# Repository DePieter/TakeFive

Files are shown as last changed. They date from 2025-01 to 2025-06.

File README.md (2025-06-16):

# Take Five

Take Five is een innovatief systeem dat zorgverleners in woonzorgcentra helpt hun stressgrens beter te bewaken door stress op een niet-verstorende manier bespreekbaar en beheersbaar te maken via een combinatie van een slimme wearable, een realtime feedbackunit en een optionele verificator.

**Projectteam:** Demaegdt Pieter, Tops Bram, Schrijvers Finn  
**Datum:** 23/05/2025

## Samenvatting

> _Goede zorg start bij goede zelfzorg._

Zorgverleners ervaren vaak hoge werkstress, wat kan leiden tot burn-out. Omdat stress doorgaans te laat wordt herkend en aangepakt, is het belangrijk om vroegtijdige signalen zichtbaar te maken. Take Five biedt een persoonlijk hulpmiddel dat aangeeft wanneer stress echt te veel wordt, zodat zorgverleners tijdig kunnen ingrijpen.

Het systeem bestaat uit drie componenten:

- **Wearable:** detecteert fysiologische stresssignalen zoals hartslagvariatie (HVR) en cortisol. Bij een te hoog stressniveau trilt het apparaat zacht, met een aangenaam ritme. Indien de stress te lang aanhoudt, volgt een duidelijkere trilling.
- **Feedbackunit (FU):** toont enkel aan de desbetreffende gebruiker het realtime stressniveau op een visuele en discrete manier.
- **Verificator (optioneel):** stelt gebruiker in staat om zich te laten begeleiden bij wetenschappelijk onderbouwde oefeningen. De gebruiker scant zichzelf in, waarna een geschikte pauze wordt voorgesteld. Hierbij is een ingebouwde tijdslimiet per persoon om misbruik te voorkomen.

> _Take Five maakt stress zichtbaar, ondersteunt zelfzorg en draagt bij aan een gezonde, collegiale werkomgeving._

<p align="center">
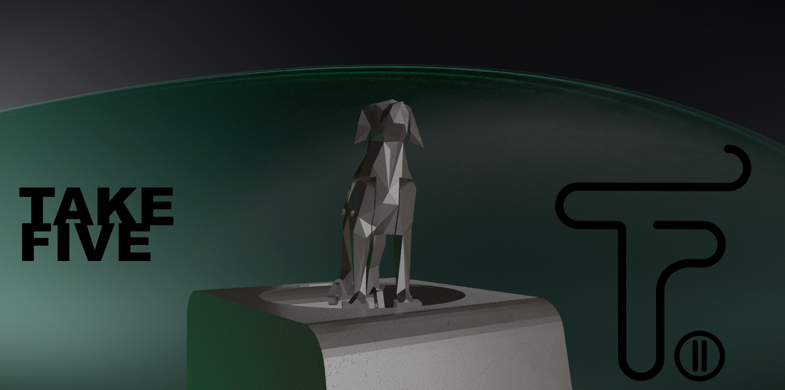
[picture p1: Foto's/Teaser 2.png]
  
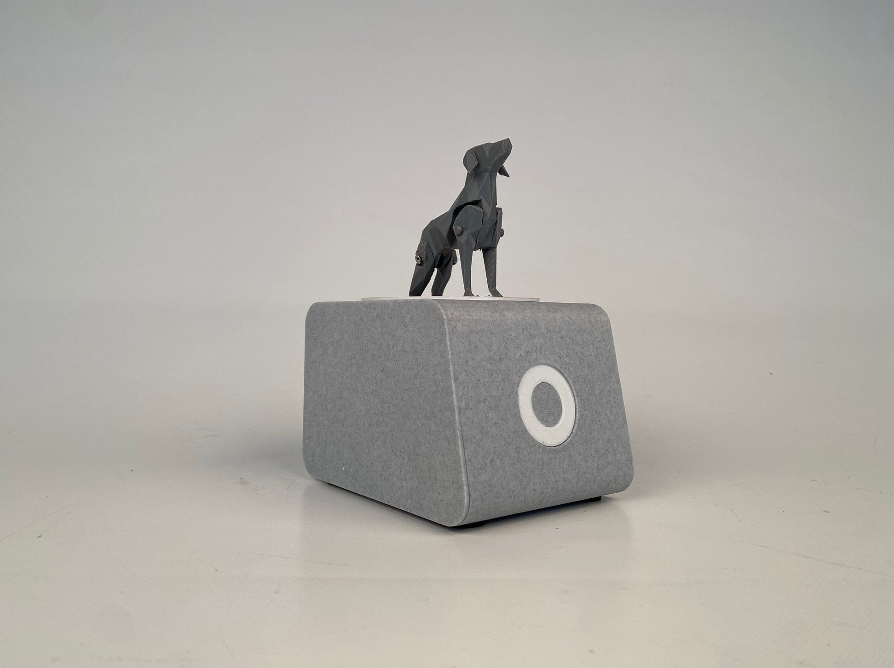
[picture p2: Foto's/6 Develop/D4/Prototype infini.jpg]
  
</p>

## Introductie

In de Belgische zorgsector loopt één op de vijf verpleegkundigen een groot risico op burn-out, en bijna 40% van de zorgverleners ervaart te veel werkstress [^1]. Dit probleem leidt tot ziekteverzuim en hoge kosten: in 2021 werd meer dan 1,8 miljard euro besteed aan arbeidsongeschiktheid door burn-out en depressie, een stijging van 59% sinds 2016 [^2]. Zorgverleners missen echter vaak directe en persoonlijke feedback over hun stressniveau, waardoor tijdig ingrijpen uitblijft.

> _Ieder jaar wordt er 280 miljoen euro gespendeerd aan burn-outs in de zorgsector._  
> _Op welke manier kan de stress bij woonzorgmedewerkers verlaagd worden zonder dat dit het werk verstoort?_

## Doelstelling

Een laagdrempelig en persoonsgericht systeem ontwikkelen dat zorgverleners helpt hun stressniveau tijdig te herkennen en te beheersen. Take Five stimuleert zelfzorg, voorkomt burn-out en versterkt het welzijn van zorgpersoneel.

Dit project focust specifiek op de toepassing binnen **woonzorgcentra (WZC)**.

[^1]: Cijfers uit de Belgische gezondheidszorgstudie 2022  
[^2]: RIZIV-rapport over arbeidsongeschiktheid, 2021

## Methodologie
In de eerste discoverfase werd de opdracht verkend aan de hand van de designchallenge 'Werkbaar Werk in de Zorg', waarbij user interviews en een literatuuronderzoek bevestigden dat stress op de werkvloer een groot probleem vormt. Methodes zoals de 5WH- en PESTEL-analyse hielpen om de onderliggende noden en kerninzichten te identificeren.
In de definitiefase werd het probleem verder verkend via een praktische aanpak met als leidraad "fall in love with the problem, not the solution." Er werden snel eerste prototypes ontwikkeld en getest in WZC Altus, waarna een verbeterde versie een week lang werd getest bij WZC De Oever. Een groepsinterview sloot de testfase af, en de verzamelde feedback vormde de basis voor het verfijnen van de design requirements die waardevol zijn in de volgende fase.
In de ontwikkelfase werd het concept verder verfijnd via gebruikerstesten en ideation-sessies met onder andere brainstorming, rollenspellen, Think Aloud en Wizard of OZ-methodes. Op basis daarvan werden prototypes uitgewerkt en getest in verschillende woonzorgcentra.
Tijdens deze tests werd gebruikgemaakt van technieken zoals Emotional Mapping met Plutchik’s Wheel, card sorting en dot-voting om emotionele reacties van gebruikers in kaart te brengen. De resultaten werden geanalyseerd met de MoSCoW-methode om prioriteiten te bepalen voor verdere verbetering.
Om ontwerpkeuzes doelgericht te evalueren, werden A/B-tests, heuristic evaluations, SUS-enquêtes en observaties ingezet. Dit leverde concrete inzichten op in wat wel en niet werkt.
Als laatst werd een online enquête verspreid om voorkeuren rond visuele en esthetische elementen te onderzoeken. Hierbij werd rekening gehouden met bias via technieken zoals desirability testing, preference testing en 5 second testing. De resultaten dienden als input voor de uiteindelijke stijl- en vormkeuzes.
De volledige ontwerpmethodologie is visueel samengevat in de onderstaande tijdlijn.

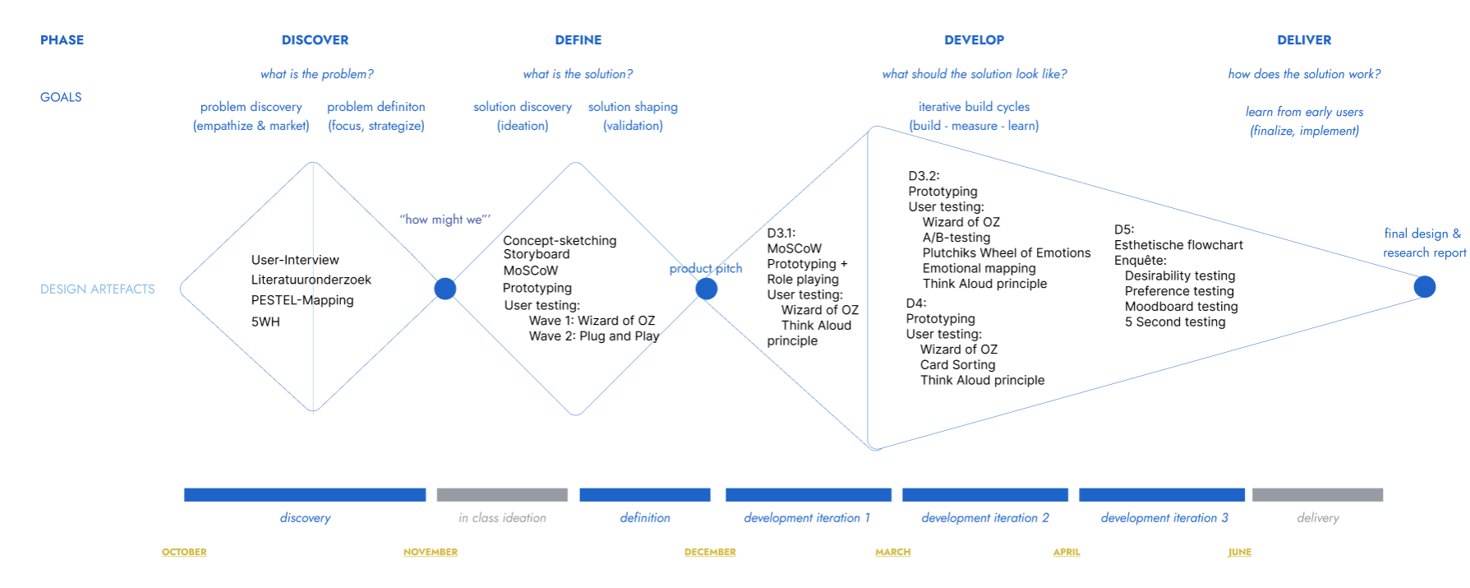
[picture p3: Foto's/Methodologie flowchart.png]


## Discovery
De discoveryfase richt zich op het definiëren van de probleemruimte, nog niet op het maken van een product. Via user interviews wordt bepaald welke problemen prioritair zijn, wat resulteert in een goed geformuleerde "how might we".

### Doelstelling
Een heldere "how might we" formuleren binnen de probleemruimte.

### Materiaal & Methoden:

-User interviews (N=3)

-Literatuuronderzoek (N=10)

### Literatuuronderzoek
Literatuuronderzoek ([Research report: literature reviews](Reports/Discovery/Research%20report%20literature%20reviews.pdf)) heeft de probleemruimte duidelijker in kaart gebracht, zo blijkt dat de zorgsector sinds 2019 kampt met een structureel hoge werkdruk, waarbij vooral het zorgpersoneel zwaar wordt getroffen. In 2023 liep 14,4% van de zorgmedewerkers risico op een burn-out[^3]. Deze problematiek is het sterkst aanwezig in woonzorgcentra, waar het aantal medewerkers met burn-outsymptomen tussen 2013 en 2023 met 7,2% is gestegen. In combinatie met de toenemende vergrijzing maakt dit de sector bijzonder kwetsbaar.

Werkdruk wordt als de belangrijkste oorzaak van werkstress geïdentificeerd. Bij 41,8% van de zorgmedewerkers heeft dit een negatieve impact op zowel hun werk-privébalans als hun algemeen welzijn[^4]. Verpleegkundigen en zorgkundigen in woonzorgcentra ervaren de hoogste werkdruk en vormen daarom de primaire doelgroep van dit project.

Sinds de coronapandemie is het langdurig ziekteverzuim met 50% gestegen. De economische impact van burn-out is aanzienlijk: jaarlijks kost het de zorgsector naar schatting 228 miljoen euro, een stijging van 10% in vijf jaar tijd. Hoewel er reeds interventies bestaan, zoals korte dagelijkse check-ups, blijkt de effectiviteit daarvan voorlopig beperkt.
In onderstaande foto wordt de probleemruimte concreet weergegeven:

<div align="center">
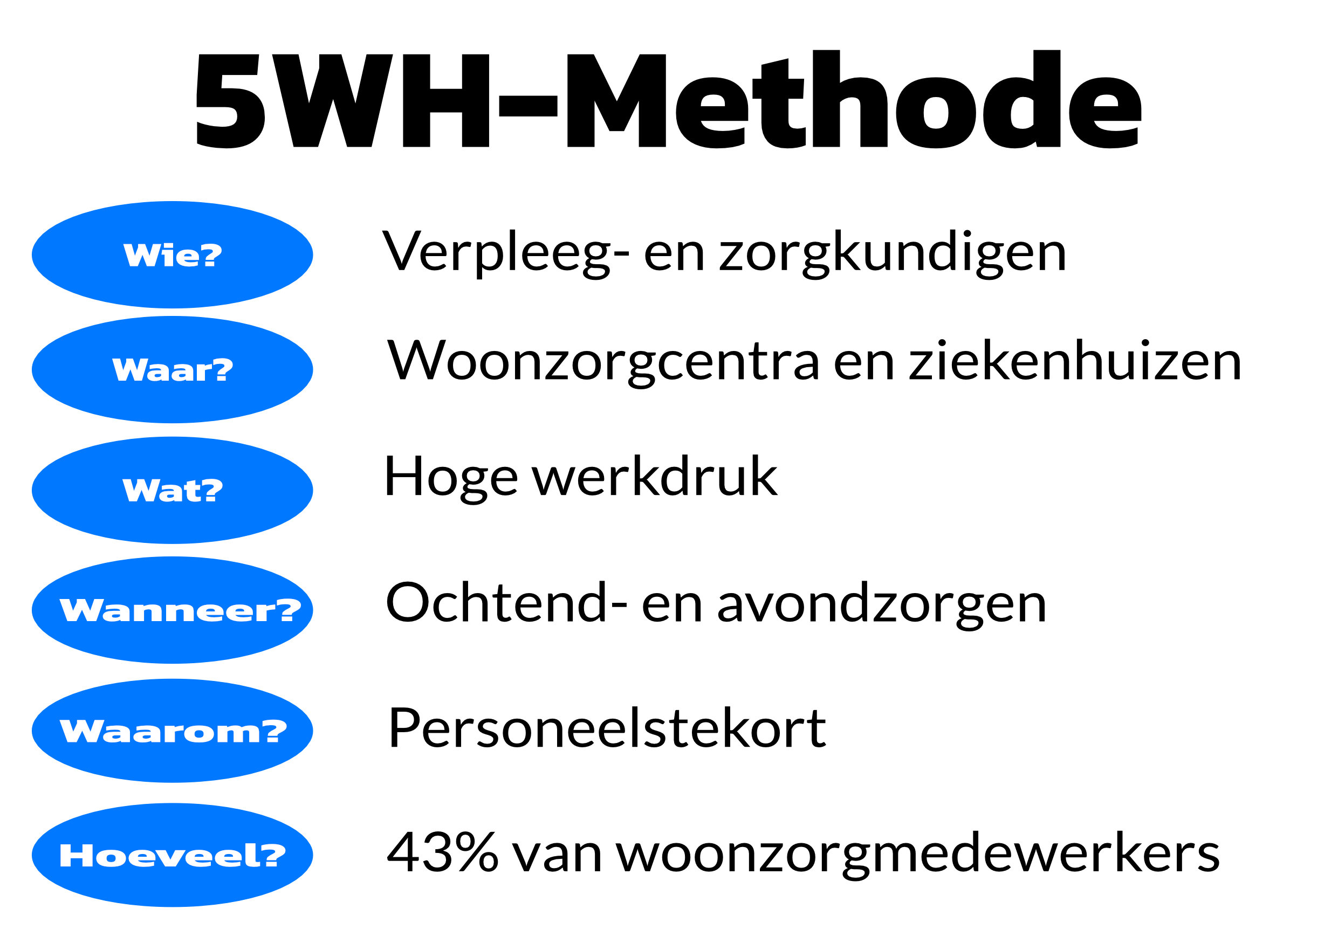
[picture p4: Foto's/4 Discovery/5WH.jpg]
  
</div>

[^3]: Vlaamse Overheid. (2023). Werkbaar werk in de zorg- en welzijnssector: Samenvatting.
[^4]: (Sociaal-Economische Raad van Vlaanderen, 2023)

### Haalbaarheid
Het is al snel duidelijk dat het in dit project van belang is om stress meetbaar te maken. Hieromtrend richt het haalbaarheidsonderzoek zich op het meten van biomarkers om werkstress en burn-out in de zorgsector objectief te detecteren. Chemische biomarkers, zoals het C-reactief proteïne in bloed of speeksel, blijken moeilijk frequent meetbaar in de praktijk. Fysische biomarkers, zoals hartslagvariabiliteit (HRV), worden daarentegen als het meest haalbaar beschouwd.

### User Interviews (N=3) 
Het doel van deze interviews was om inzicht te krijgen in hoe verpleegkundigen werkdruk ervaren en hoe dit zich vertaalt naar stress en burn-out in hun dagelijkse praktijk. Omdat stress een subjectieve ervaring is die sterk verschilt per persoon, werd gekozen voor **contextual inquiries**: een open, verkennende interviewmethode die inzichten oplevert binnen de echte werkcontext van de zorg.

Er werden drie interviews afgenomen bij **studenten verpleegkunde**, geselecteerd via **purposive sampling**. Door hun stages hebben deze studenten ervaring met verschillende afdelingen (zoals geriatrie en woonzorgcentra) en kunnen ze zowel praktijkgericht als reflectief naar het probleem kijken. Deze proef was niet bedoeld om statistisch representatief te zijn, maar om *diepgang* te bieden en **oorzaak-gevolgrelaties** te identificeren.

Bij elk interview werden **5WHY’s** en een **PESTLE-analyse** gebruikt als theoretisch kapstok:

Enkele relevante uitspraken:

>“Door personeelstekort sla ik vaak mijn korte pauze over.”

>“Als er nog veel patiënten geholpen moeten worden, stel ik mijn middagpauze uit.”

Hieruit blijkt dat vaste pauzemomenten vaak niet genomen worden wanneer werkdruk dit niet toelaat.

### PESTLE 
De **PESTLE-analyse** werd gebruikt als gesprekskader tijdens de interviews om de externe invloeden op werkdruk te analyseren. Deze dimensies werden onderzocht:

- **Political:** Beleid rond personeelsinzet en pauzeplanning
- **Economic:** Kosten van ziekteverzuim en burn-out
- **Social:** Collega's die geen pauzes nemen → sociale norm
- **Technological:** Beperkingen en kansen van wearables in de zorg
- **Legal:** Arbeidswetgeving rond rusttijden
- **Environmental:** Werkomgeving en logistieke indeling van afdelingen

Hoewel studenten niet de primaire doelgroep zijn voor het eindproduct, boden zij **waardevolle inzichten in de dagelijkse realiteit op de werkvloer**. Op basis van deze bevindingen wordt aanbevolen om in vervolgonderzoek ook leidinggevenden en directies te betrekken, om structurele oplossingen in kaart te brengen.

### Oorzaken & Gevolgen
Personeelstekort in de zorg leidt tot langere shifts en het inkorten of zelfs overslaan van pauzes, wat de ervaren stress bij zorgmedewerkers verder verergert. Hierdoor ontstaat een dubbel negatief effect: de verhoogde werkdruk zorgt niet alleen voor meer stress, maar vermindert tegelijkertijd ook de mogelijkheid tot herstel. Deze combinatie maakt de situatie bijzonder kwetsbaar. De burn-outproblematiek binnen de sector blijft toenemen en brengt stijgende kosten met zich mee, wat de noodzaak onderstreept voor preventieve maatregelen. Werkdruk die hoofdzakelijk wordt veroorzaakt door personeelstekort blijkt daarbij de voornaamste oorzaak van stress, versterkt door het ontbreken van structurele oplossingen.

### Conclusie 
Het doel van deze fase was het verkennen en afbakenen van de probleemruimte binnen de zorgsector, met een focus op werkdruk, stress en burn-out. Door middel van kwalitatieve interviews, literatuurstudie en het toepassen van de 5WHY- en PESTLE-methodologieën werd meermaals duidelijk dat:

- Pauzes een cruciale maar onderbenutte herstelstrategie zijn.
- Werkdruk toeneemt door personeelstekort en hoge zorgzwaarte.
- Technologische ondersteuning potentieel heeft, mits aangepast aan de context en noden van de gebruikers.

Deze inzichten hebben geleid tot de eerste set van **design requirements**, die de basis vormen voor het volgende projectonderdeel: de definitiefase en conceptontwikkeling van een oplossing die zorgverleners ondersteunt bij stressmanagement.
In deel [product design requirements](#product-design-requirements) staat een overzichtstabel met alle design requirements voor het eindproduct.

| ID   | Design Requirements                                                                                                                                       | Source    |
| ---- | --------------------------------------------------------------------------------------------------------------------------------------------------------- | --------- | 
| DR01 | Het ontwerp moet flexibel inspelen op wisselende personeelsbezetting gedurende de dag, zodat het inzetbaar blijft bij schommelingen in beschikbaarheid.   | Discovery |
| DR02 | Het systeem of de ruimte moet extra ondersteuning bieden tijdens piekmomenten, met name tijdens ochtend- en avondzorg, waarin de werkdruk het hoogst is.  | Discovery |
| DR03 | Het ontwerp moet flexibele pauzemomenten faciliteren, afgestemd op het actuele zorgritme, in plaats van vaste tijdsintervallen.                           | Discovery |
| DR04 | Het ontwerp moet bijdragen aan een rustgevende en stressverlagende omgeving door middel van passieve elementen zoals licht, kleur en geluid.              | Discovery |
| DR05 | Het product moet inspelen op uiteenlopende gebruikerservaringen en zowel stressverlichting (pain relief) als positieve meerwaarde (value promise) bieden. | Discovery |
| DR06 | Hartslagvariabiliteit (HRV) moet worden gebruikt als de primaire biomarker voor het meten van stressniveaus en herstelmomenten.                           | Discovery | 

## Definition
In de definitiefase worden mogelijke oplossingen onderzocht voor het eerder gedefinieerde probleem, met als doel een onderbouwde conceptkeuze. Dit concept vormt de basis voor verdere ontwikkeling in de develop- en deliverfases. De definitiefase bestaat uit drie waves, waarvan één al deels in de developfase zit. Per wave wordt het concept verder verfijnd aan de hand van theoretische modellen.

### Doelstellingen
- Ontwikkelen van prototypes die een doordacht concept representeren.
- Testen van deze prototypes in realistische scenario’s om haalbaarheid te verifiëren.
- Inzichten en gebruikersfeedback verzamelen voor verdere verbetering.

### Materiaal & methoden
Twee (+1) waves die gebruik maken van volgende methodologiën:
- Ideation
- Storyboarding
- MoSCow
- Prototyping 
- User testing (Wizard of Oz + Plug & Play)

---

### **Wave 1 (N=5)**
In deze eerste wave staat verkenning centraal: het vinden van de juiste oplossing is nog onzeker, maar de eerste ideeën, prototypes en tests vormen een cruciale stap om grip te krijgen op stress op de werkvloer.

#### Ideation
In de eerste ontwikkelingsfase werd al snel gefocust op een wearable die stress meet en feedback geeft. De vorm hangt af van de draaglocatie, die beperkt wordt door medische richtlijnen (bv. geen pols wegens infectierisico) en nauwkeurigheid van hartslagmeting. Drie locaties bleven over: borst, bovenarm en benen. De benen vielen af vanwege mogelijke associaties met enkelbanden.
Vervolgens werden snel eenvoudige schetsen gemaakt om het concept visueel te verkennen.

<p align="center">
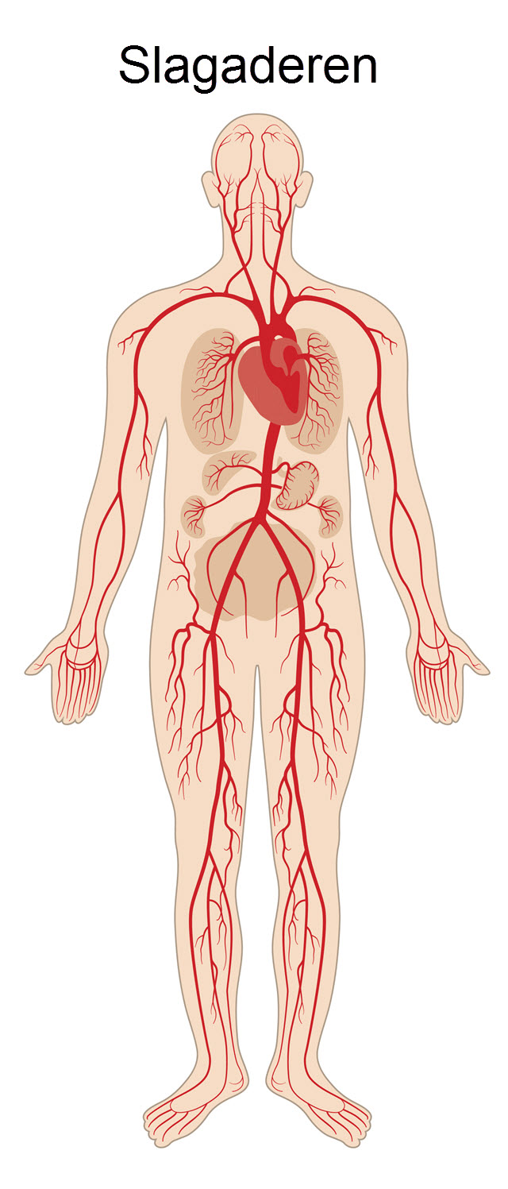
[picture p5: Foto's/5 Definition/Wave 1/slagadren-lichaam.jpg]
  
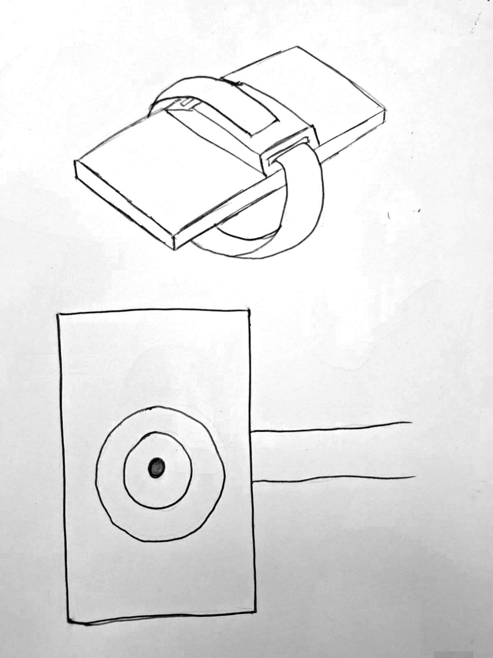
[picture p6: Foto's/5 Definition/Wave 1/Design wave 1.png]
  
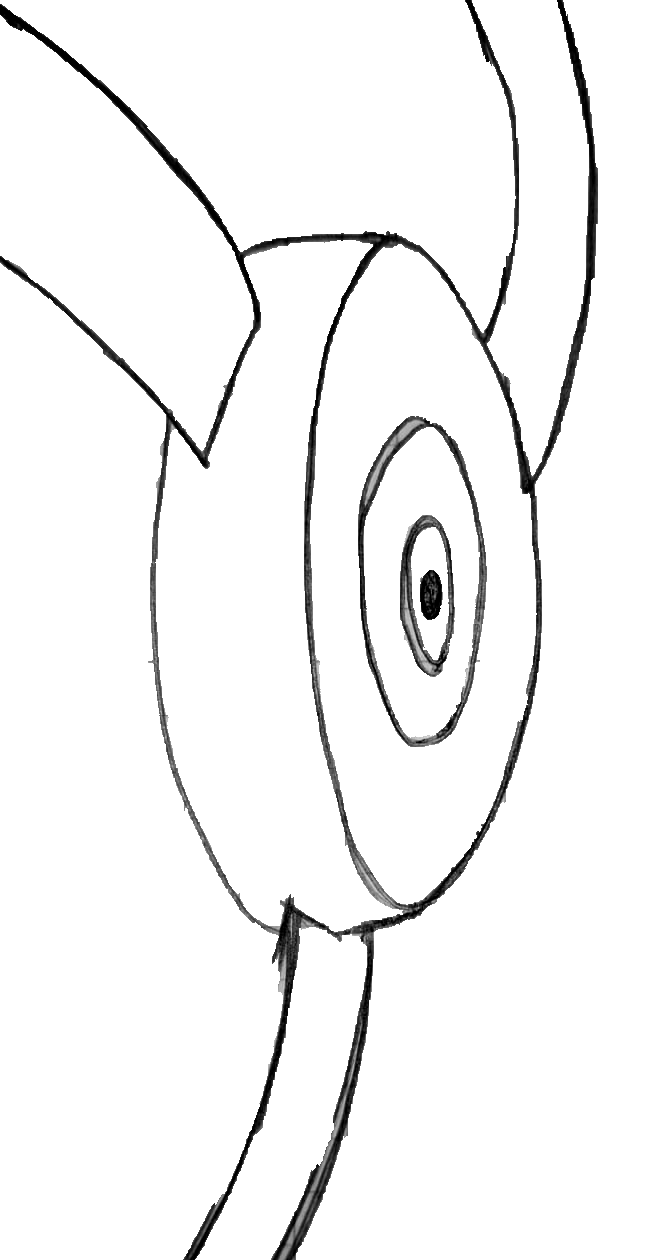
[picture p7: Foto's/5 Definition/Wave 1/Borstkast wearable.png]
  
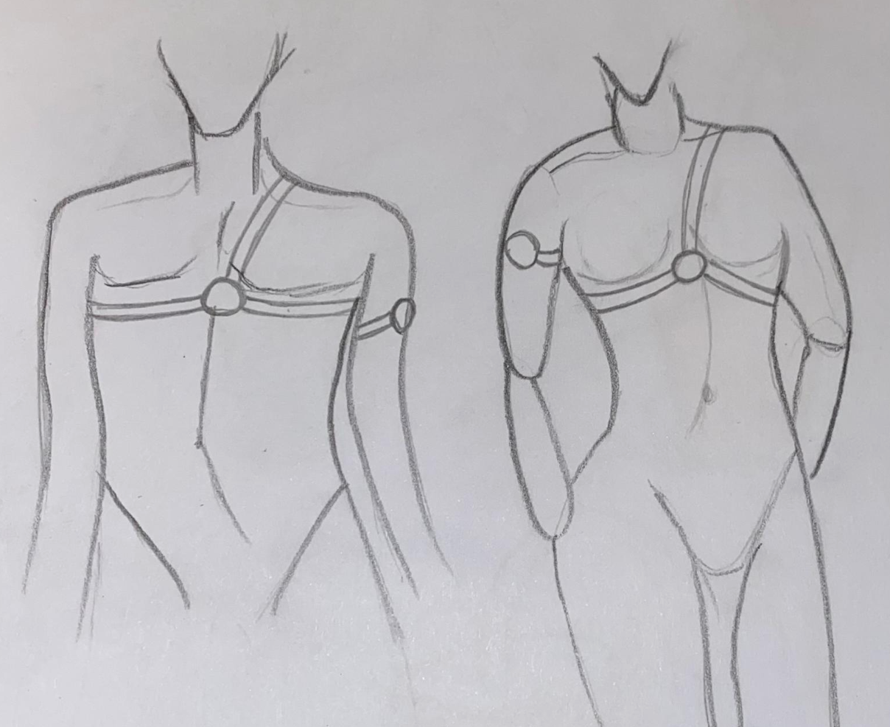
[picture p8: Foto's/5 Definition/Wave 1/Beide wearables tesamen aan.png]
  
</p>

#### Storyboarding
Om eerste onvoorziene fouten in het wearable-concept op te sporen, werd een storyboard opgesteld. Dit geeft een eerste inzicht in de werksituatie en mogelijke basisfouten.

Scenario: De zorgverlener komt aan, neemt de wearable en activeert die, waarop een lichtsignaal verschijnt. Enkele uren later volgt een trilling als teken van verhoogde stress. De zorgverlener neemt kort pauze (water drinken, diep ademhalen) en hervat daarna het werk. Na de shift wordt de wearable opgeladen.

<p align="center">
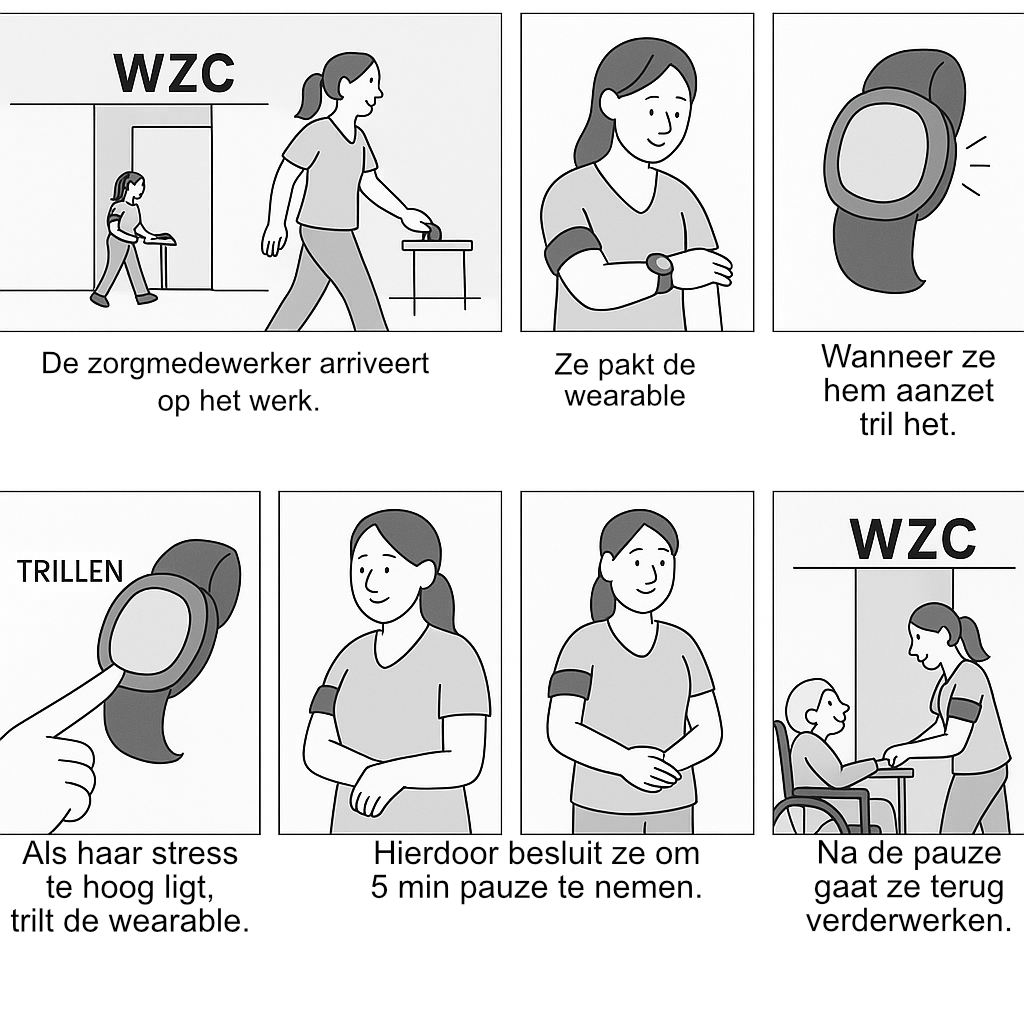
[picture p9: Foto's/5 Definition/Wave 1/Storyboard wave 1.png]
  
</p>

#### MoSCow
Om een eerste idee te krijgen van enkele voorwaarden waaraan de wearable moest voldoen, werd een eerste MoSCoW-analyse uitgewerkt.

<table>
  <tr>
    <th>Must</th>
    <td>
      - Aangename feedback<br>
      - Goedkoop<br>
      - Comfortabel zijn<br>
      - Altijd aanwezig zijn<br>
      - Oplaadbaar zijn<br>
    </td>
  </tr>
  <tr>
    <th>Should</th>
    <td>
      - Eén vaste locatie<br>
      - Makkelijk schoon te maken<br>
      - Licht geven<br>
      - Wifi-verbinding<br>
    </td>
  </tr>
  <tr>
    <th>Could</th>
    <td>
      - Leuk uitzien<br>
      - Hogerop verwittigen<br>
      - Snoozbaar zijn<br>
      - Teambuilding pauzes<br>
    </td>
  </tr>
  <tr>
    <th>Wouldn't</th>
    <td>
      - Luid zijn<br>
      - Opdringerig zijn<br>
      - Storend zijn<br>
      - Ongewenste gebruikersaantrekkingen<br>
    </td>
  </tr>
</table>

#### Prototyping
Er zijn vier verschillende prototypes ontwikkeld: twee voor de feedbackunit en twee voor de sensor. Dit maakt het mogelijk om met meerdere testpersonen tegelijk te testen.

Momenteel is het nog niet duidelijk of het voldoende is om de feedback te laten gebeuren via de wearable of dat er een externe feedbackunit nodig is. Om deze reden is er ook een extra concept voorzien bij het mken van prototypes; de feedbackunit (FU).

Voor de feedbackunit zijn alle mogelijke signaleringsmethoden geïntegreerd in twee compacte wizard of oz prototypes, die op afstand kunnen worden aangestuurd via een smartphone. Hieronder worden de prototypes weergegeven en beschreven.

<table>
  <tr>
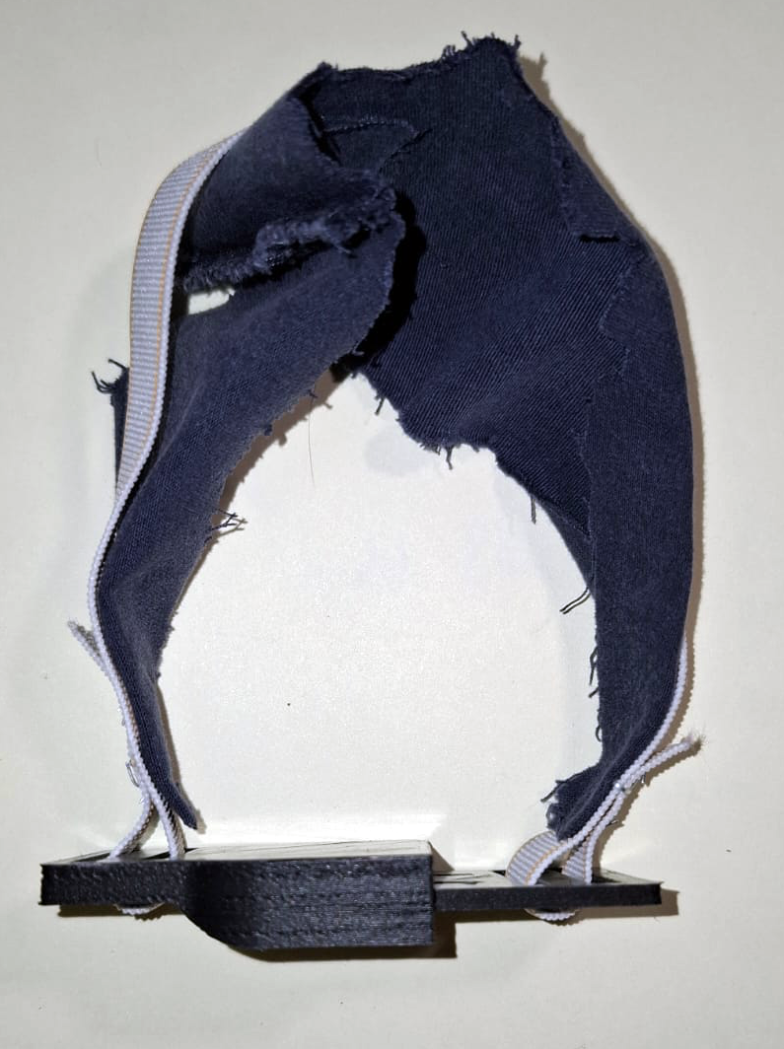
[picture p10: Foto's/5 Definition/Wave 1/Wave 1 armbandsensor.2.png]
    <td>
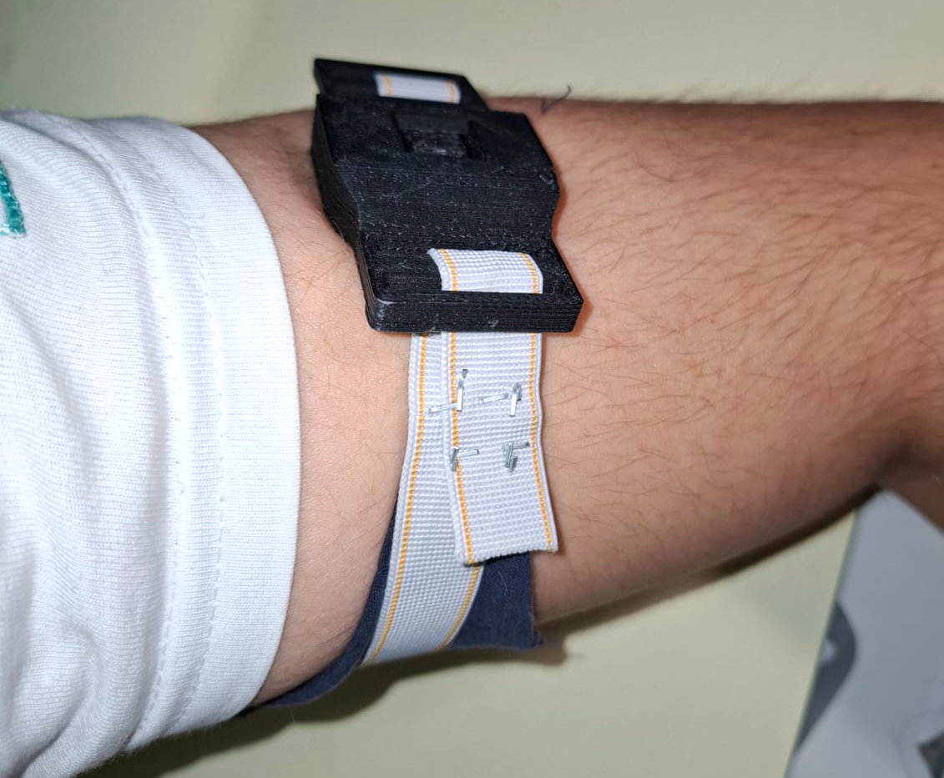
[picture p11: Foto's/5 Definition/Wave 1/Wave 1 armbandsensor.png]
	  <td>
    <td>De <b><u>armband sensor:</u></b> bestaat uit een ge-3D-printe body met een elastieken band, deze kan gedragen worden op de bovenarm.</td>
  </tr>
  <tr>
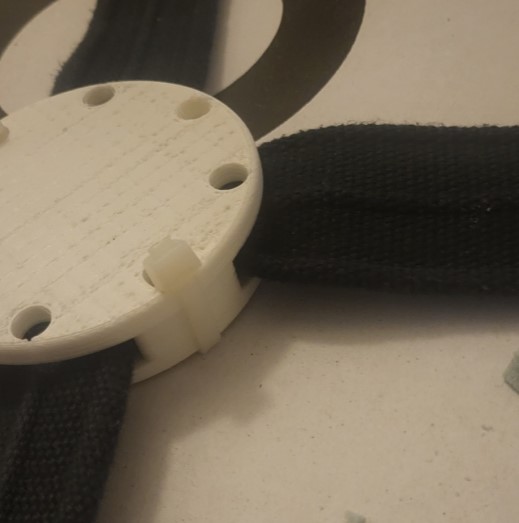
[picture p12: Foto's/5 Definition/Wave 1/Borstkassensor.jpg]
    <td>
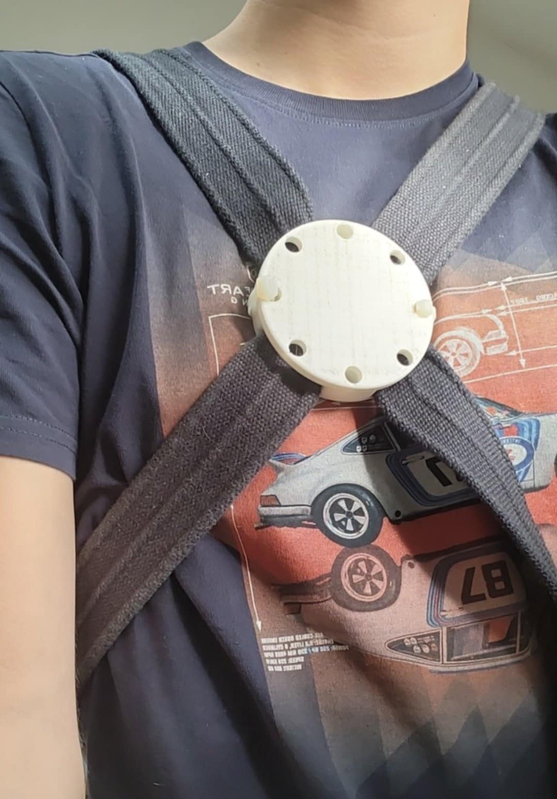
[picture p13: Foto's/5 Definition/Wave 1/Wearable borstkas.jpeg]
	  <td>
    <td>De <b><u> borstkas sensor</u></b> bestaat uit twee verstelbare riemen met een 3D-geprinte behuizing, zodat hij naar wens kan worden aangespannen. <b><u>          </td></td>
  </tr>
  <tr>
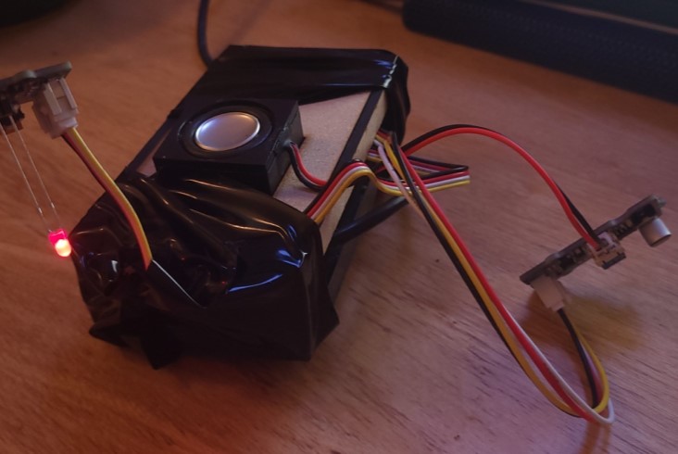
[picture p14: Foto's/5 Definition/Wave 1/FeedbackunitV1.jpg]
    <td>
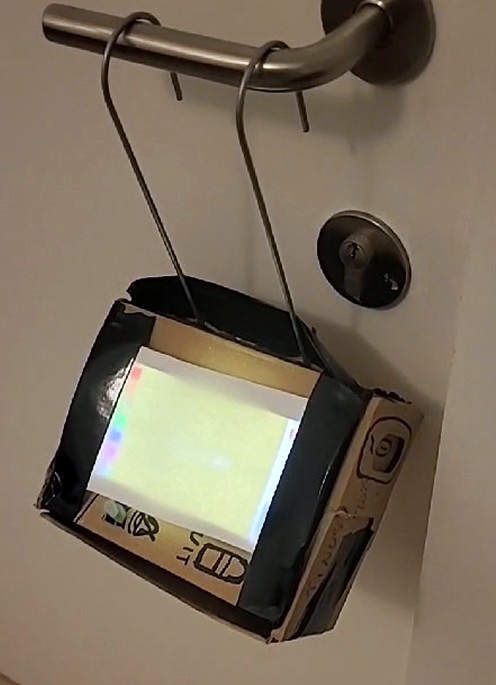
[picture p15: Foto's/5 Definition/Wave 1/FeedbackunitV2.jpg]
	  <td>
    <td>De <b><u>feedback unit's:</u></b>  bestaan uit een MDF- en een kartonnen behuizing, waarmee alle signaalmethoden, zoals geluid en licht, getest kunnen worden met Arduino en een ingebouwde gsm.    </td></td>
  </tr>
</table>

#### User testing (n=5)
Tijdens deze gebruikerstest in WZC Althus werden de eerste functionele prototypes van het stressdetectiesysteem geëvalueerd. Doel was het concept te toetsen op levensvatbaarheid, gebruiksvriendelijkheid en impact, om zo richting te geven aan verdere ontwikkeling.
Vijf zorgmedewerkers (begeleiders, opvoeders, teamleider) werden geïnterviewd na een korte introductie en informed consent. Ze vertelden over hun werk, stresservaringen, copingstrategieën en gaven feedback op de prototypes (zie [Protocol wave 1](https://github.com/DePieter/TakeFive/blob/main/Protocols/Define/Wave%201%20Protocol%20Althus.pdf)).

Tijdens het interview konden de respondenten ook de prototypes zelf ervaren. Hierbij werd gepeild naar hun ervaring met deze meldingsvormen: waren ze storend of net ondersteunend? Waren ze duidelijk en bruikbaar in een drukke werkomgeving?

Respondenten ervaren stress door tijdsdruk, onverwachte situaties en multitasking. Men herkende structurele overbelasting en gaf aan dat hun huidige strategieën vaak tekortschieten.
Het trilsignaal van de armband werd als subtiel en niet-storend ervaren, geluidssignalen als te opdringerig. Een externe feedbackunit op de zorgkar werd gezien als nuttige aanvulling, aangezien trillingen soms onopgemerkt blijven.
Meteen pauze nemen op basis van meldingen bleek zelden haalbaar, maar vroegtijdige signalering werd als waardevol beschouwd. De behoefte aan een compact, discreet en intuïtief systeem dat naadloos past in de workflow werd breed gedeeld.
De inzichten zijn verwerkt tot ontwerpvereisten in 
[Rapport wave 1](https://github.com/DePieter/TakeFive/blob/main/Reports/Define/Rapport%20Althus.pdf).

> _"Het zou handig zijn als een systeem stress kan detecteren voordat het te erg wordt."._

> _"Een discreet signaal, zoals een trilling, zou helpen zonder cliënten te storen."._

> _"Als ik zou kunnen kiezen, kies ik voor de armband."._

> _"Een discreet signaal, zoals een trilling, zou voorkomen dat gebruikers geïrriteerd of boos worden."._

> _"Ik vind de externe feedbackunit een goed concept omdat ik in the heat of the moment zo'n trilling via enkel de wearable niet altijd zal opmerken vrees ik"._

#### Conclusies & implicaties:
Het hoofddoel van wave 1 was om de conceptuele werking goed of af te keuren. Daarbij werd onderzocht of het gebruik van een feedbackunit effectief en zinvol is. Dankzij waardevolle inzichten uit onder andere de eerste gebruikerstesten, levert deze test niet alleen een antwoord op de hoofdvraag, maar maakt ze het ook mogelijk om al enkele ontwerpdetails vast te leggen. De conclusie is dat het concept verder uitgewerkt kan worden, met de feedbackunit als essentieel element om triggerblindheid te voorkomen. Daarbij moet rekening gehouden worden met de [Product design requirements](#product-design-requirements) waarvan hieronder de belangrijkste staan weergegeven:

| ID    | Design Requirements                                                                 | Source   | Date       |
|-------|---------------------------------------------------------------------------------------|----------|------------|
| DR07  | Subtiel design met trilling of licht, geen geluid.                                   |          |            |
| DR12  | Klein, licht en comfortabel draagbaar ontwerp.                                       |          |            |
| DR17  | Discreet en universeel ontwerp tegen stigma.                                         |  Wave 1  | 11/12/2024 |

### **Wave 2 (N=5)**
De bekomen design requirements uit wave 1 worden hier in wave 2 gebruikt om het ontwerp te verbeteren. Hierbij werd bij benadering eenzelfde structuur zoals wave 1 toegepast.

#### Ideation
Tijdens de ideatiefase van wave 2 werd in een brainstormsessie besloten om nieuwe versies van de FU en de wearable te ontwerpen met enkele werkende, primitieve functies. Dit heeft als doel om de prototypes geschikt te maken voor een meer uitgebreide tests in een realistische werkomgeving. Nadat de twee beste concepten waren geschetst, werd onderzocht hoe deze gerealiseerd konden worden.
De FU bevatte zowel de signaalfunctie als een oplaadstation.
De wearable werd voorzien van EVA-foam, gevormd met behulp van een mal zodat het goed aansluit op het lichaam.

<p align="center">
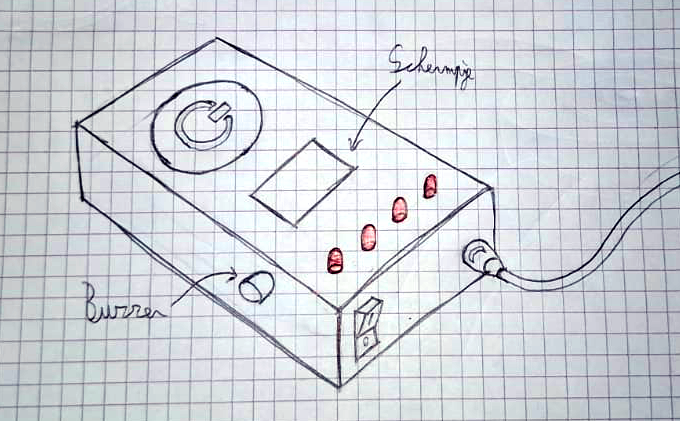
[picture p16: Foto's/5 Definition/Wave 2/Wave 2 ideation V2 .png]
  
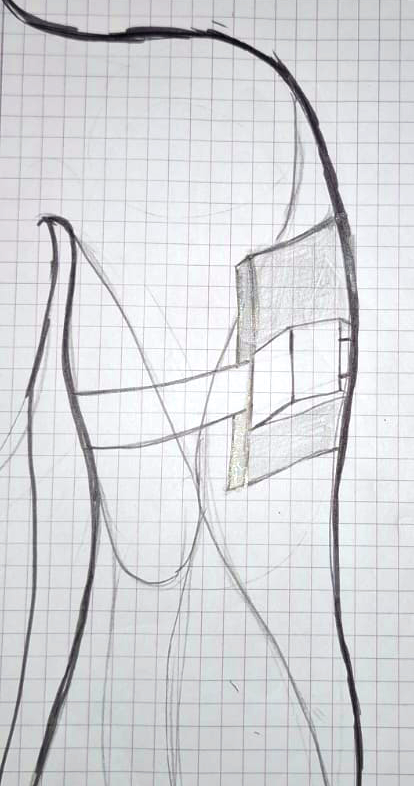
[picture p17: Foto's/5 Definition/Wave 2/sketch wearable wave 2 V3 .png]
  
</p>  

#### Prototyping
Verderwerkend op de keuzes die gemaakt zijn in de ideation, worden enkele prototypes uitgewerkt. 

<table>
  <tr>
    <td>
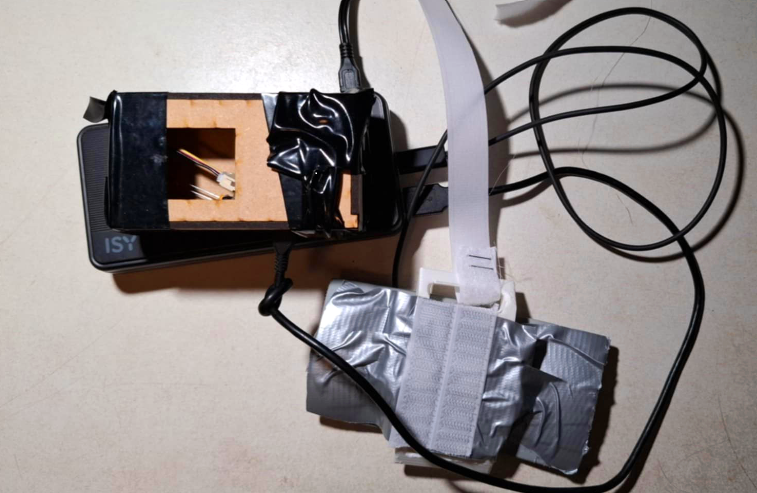
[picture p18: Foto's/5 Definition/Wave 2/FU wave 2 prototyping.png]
FU wave 2 prototyping
      
    </td>
    <td>
      De FU maakt gebruik van lichtsignalen en geluid om te communiceren. Ook beschikt de FU over een oplaadstation voor de wearable.
    </td>
  </tr>
  <tr>
    <td>
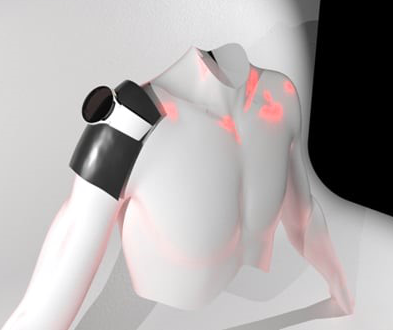
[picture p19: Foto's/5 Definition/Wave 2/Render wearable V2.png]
Render wearable V2
      
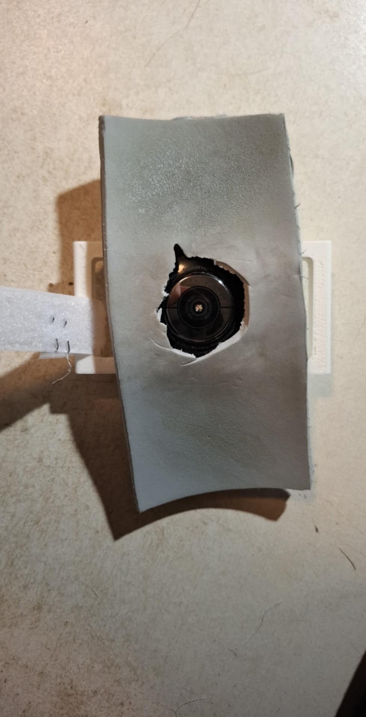
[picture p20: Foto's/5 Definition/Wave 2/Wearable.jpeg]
Wearable
      
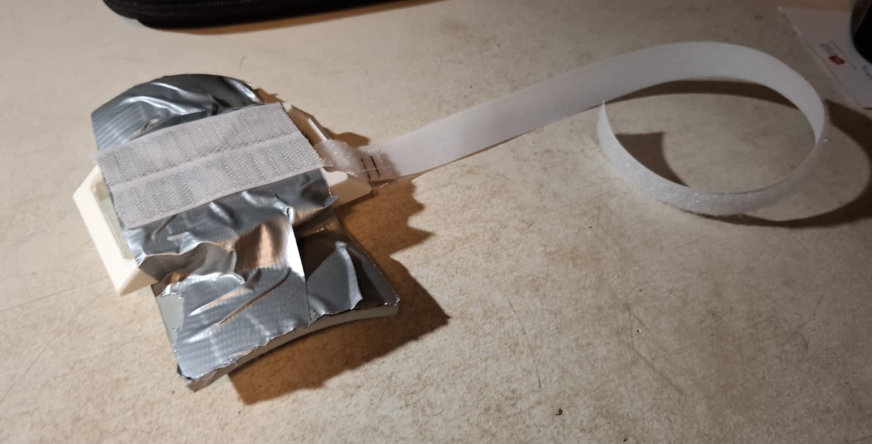
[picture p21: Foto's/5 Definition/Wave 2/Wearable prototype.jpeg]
Wearable prototype
      
    </td>
    <td>
      De wearable is vervaardigd van EVA-foam, gevormd naar de mal van een bovenarm. Daarnaast is er een smartwatchsensor geïntegreerd voor nauwkeurige stressmetingen.
    </td>
  </tr>
</table>

#### User testing (n=5)
Voor deze testfase werd een ‘Plug and Play’-protocol (zie [Protocol wave 2](https://github.com/DePieter/TakeFive/blob/main/Protocols/Define/Wave%202%20Protocol%20De%20Oever.pdf) ) ontwikkeld waarmee de zorgverleners van WZC De Oever zelfstandig aan de slag konden. Elke deelnemer kreeg een uitgebreide handleiding met instructies over het installeren van de wearable en feedbackunit, het uitvoeren van pauzeoefeningen (zoals ademhaling, korte babbel of buiten wandelen) en het invullen van een zelfevaluatie na elke oefening. De test liep over vijf dagen, waarbij deelnemers meerdere keren per dag door de feedbackunit visueel (via knipperlicht) werden aangespoord om een korte pauze te nemen.

Elke interventie werd geëvalueerd op effectiviteit via een scoreformulier. Deze kwantitatieve evaluatie werd aangevuld met kwalitatieve feedback in een afsluitend groepsgesprek.

### Conclusies & implicaties:
Deze testfase onderzocht de toepasbaarheid en integratie van het prototype in een realistische zorgcontext. Het systeem beantwoordt aan een concrete behoefte: de oefeningen hielpen gebruikers om stil te staan bij hun stressniveau en gaven rustmomenten, al verschilde de effectiviteit per persoon.
Lichtsignalen werden niet altijd opgemerkt in de drukte. Respondenten stelden subtiele extra signalen (zoals trilling of geluid) voor. Ook bleek er twijfel over de betrouwbaarheid van zelfgenomen pauzes, wat wijst op de nood aan terugkoppeling of controle in het systeem.
Belangrijke inzichten:
- De wearable was comfortabel voor korte duur, maar moet kleiner, zachter en robuuster voor langdurig gebruik.
- De impact op bewoners was nihil, wat de discretie bevestigt.
- De testopstelling was eenvoudig en werd zelfstandig beheerd.
- Gebruikers zouden het systeem aanbevelen aan collega’s.

Deze resultaten bieden input voor het verfijnen van de gebruikservaring, het verhogen van de effectiviteit en het aanscherpen van de functionele ontwerpcriteria. Het volledig verslag is terug te vinden in [Rapport wave 2](https://github.com/DePieter/TakeFive/blob/main/Reports/Define/Report%20De%20Oever.pdf)
Daarbij moet rekening gehouden worden met de [Product design requirements](#product-design-requirements) waarvan hieronder de belangrijkste staan weergegeven:

| ID    | Design Requirements                                                                                   | Source   | Date       |
|-------|-------------------------------------------------------------------------------------------------------|----------|------------|
| DR18  | Intuïtieve bediening met duidelijke pauzemeldingen in drukke omgevingen.                              |    |            |
| DR21  | Verstoort geen lopende taken en past in bestaande workflows.                                          |    |            |
| DR23  | Modulair systeem -> verwisselbaar voor dag en nacht shift                                             | Wave 2 | 23/12/2024   |

# Develop
De develop fase draait rond het verfijnen van het product. Hiervoor worden de fysieke ergonomie, de cognitieve en de sensoriële ergonomie geoptimaliseerd aan de hand van theorie, prototyping en testing. 
Deze fase bestaat uit drie opeenvolgende fases, elk met een specifieke focus:
1.	Extra Concepttest – In deze eerste fase wordt het initiële idee ter aanvulling van voorgaande definitionfase geëvalueerd en gevalideerd.
2.	Metafooronderzoek – Vervolgens wordt onderzocht welke metafoor het meest geschikt is voor de feedbackunit.
3.	Vorm- en emotieverfijning – Tot slot wordt de gekozen metafoor verfijnd op emotioneel vlak en wordt de esthetiek van het volledige prototype geoptimaliseerd.

### Doelstellingen
- Prototype verfijnen
- Belangrijkste design challenges identificeren door zowel theoretisch als praktisch onderzoek

### Materiaal & methoden
Tijdens deze fases worden verschillende methodologieën toegepast, waaronder:
- Brainstorming
- Enquêtes
- Emotional mapping
- Design sketches
- Storyboarding
- MoSCoW-methode
- Prototyping
- Gebruikerstesten

---
### Develop 3.1 / Wave 3 (N=5)
Hoewel de developfase zich voornamelijk richt op het verfijnen van het product, bevindt wave 3 zich deels nog in de discoveryfase. Dit komt doordat het concept is uitgebreid met extra componenten, zoals de feedback unit en de verificator. In wave 3 worden deze nieuwe componenten gevalideerd (discovery), terwijl tegelijkertijd zoveel mogelijk aspecten van de ergonomie worden getest (develop).

#### Brainstorming

Wave 2 toonde aan dat er behoefte was aan een feedbackunit (= een manier om aan te geven wanneer iemands stressniveau te hoog is). Belangrijk hierbij is dat de feedback losstaat van de wearable om triggerblindness te voorkomen.  

Om een bruikbaar idee te ontwikkelen, begon het proces met een individuele brainstormsessie per teamlid. Elk teamlid werkte één of meerdere concepten uit en beschreef alle eigenschappen op grote A3-bladen. Vervolgens werd via dotvoting bepaald welke eigenschappen waardevol waren voor het concept en welke moesten worden uitgesloten.

De brainstorming heeft geleid tot het implementeren van een systeem bestaande uit 3 verschillende componenten. Hierbij worden de componenten die reeds zijn gedefinieerd (wearable en feedbackunit) uitgebreid met een extra component; een verificator. 

Omdat uit eerdere waves bleek dat er twijfel bestaat over de betrouwbaarheid van zelfgenomen pauzes, fungeert de verificator als een vorm van controlemechanisme.
Alle componenten van het systeem worden in onderstaande tabel kort beschreven.

| Onderdeel      | Beschrijving                                                                                                                                 |
|----------------|----------------------------------------------------------------------------------------------------------------------------------------------|
| De wearable    | Dit is de sensor die door zorgverleners wordt gedragen om hun stressniveau te monitoren.                                              |
| Feedback Unit  | De feedbackunit toont op een visuele manier het real time stressniveau van de gebruiker. Deze is los van de wearable geplaatst om gewenning of negeren van signalen (trigger blindness) te voorkomen. |
| Verificator    | De verificator stelt pauzes voor en controleert of deze daadwerkelijk worden genomen.                                                       |

<p align="center">
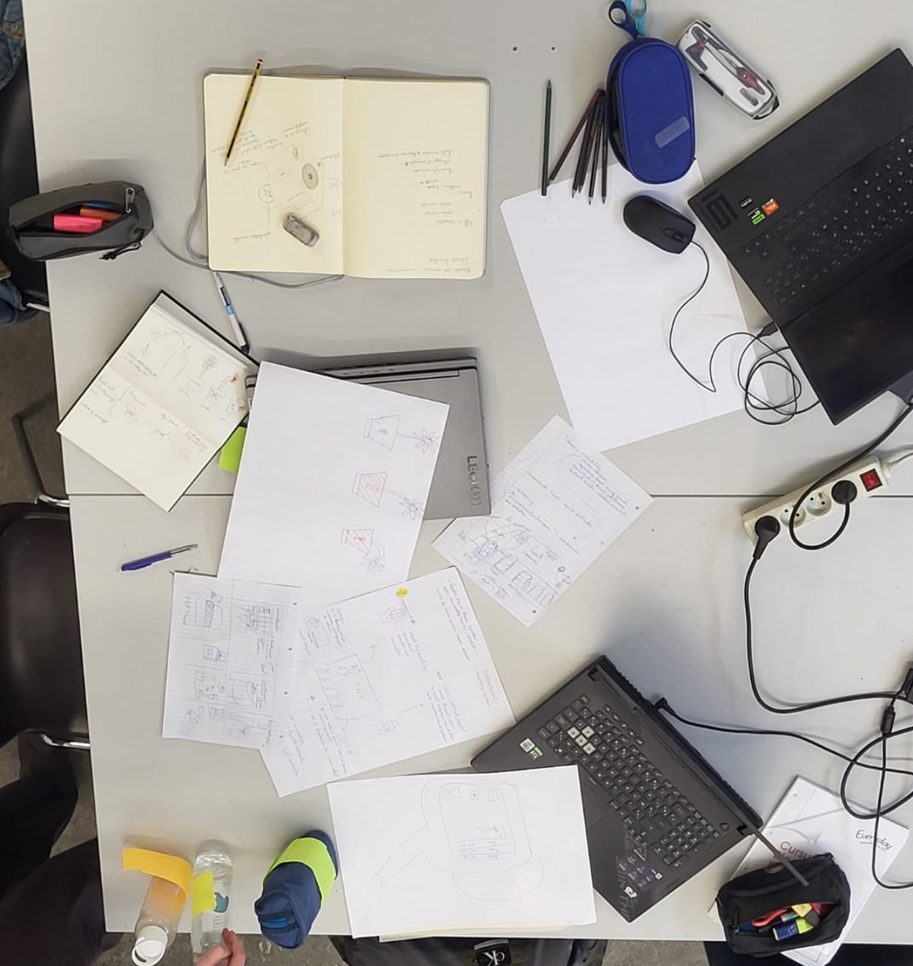
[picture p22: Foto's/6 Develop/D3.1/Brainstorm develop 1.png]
  
</p>

#### Design sketches

In de eerste versie van de feedbackunit wordt een bloem gebruikt als metafoor voor het stressniveau: naarmate de stress toeneemt, gaat de bloem zichtbaar meer hangen. De verificator wordt vormgegeven als een gieter en symboliseert de mogelijkheid om de bloem 'water te geven'. Dit gebeurt wanneer de gebruiker een voorgestelde pauze uitvoert, waarmee hij of zij actief bijdraagt aan het herstel van balans en welzijn.
| Product | Concept schetsen |
|------|------|
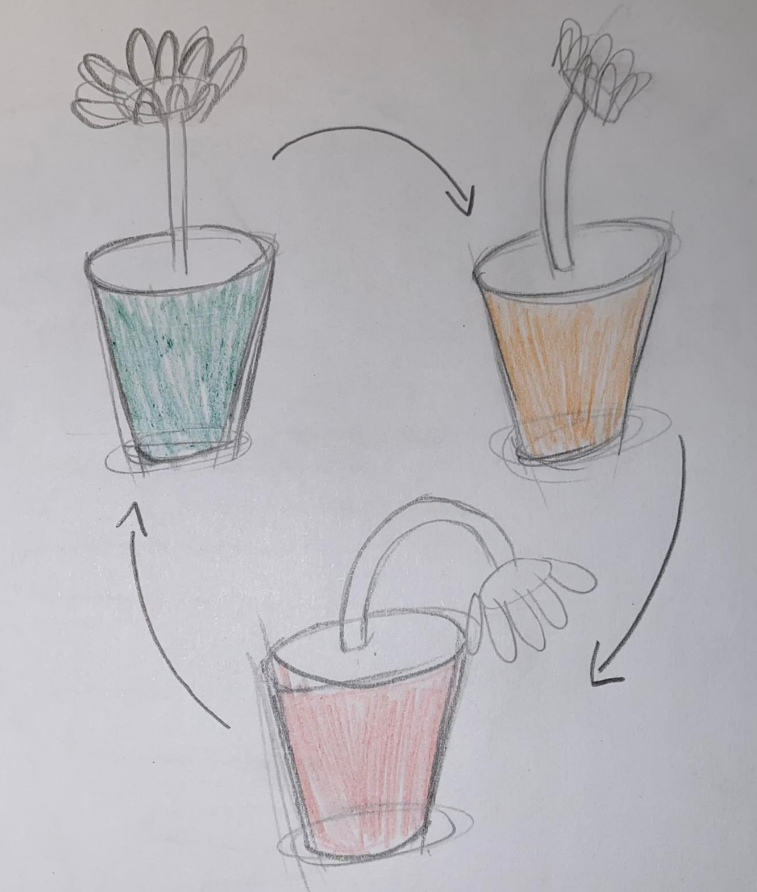
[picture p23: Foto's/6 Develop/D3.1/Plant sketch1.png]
| Feedback Unit |  |
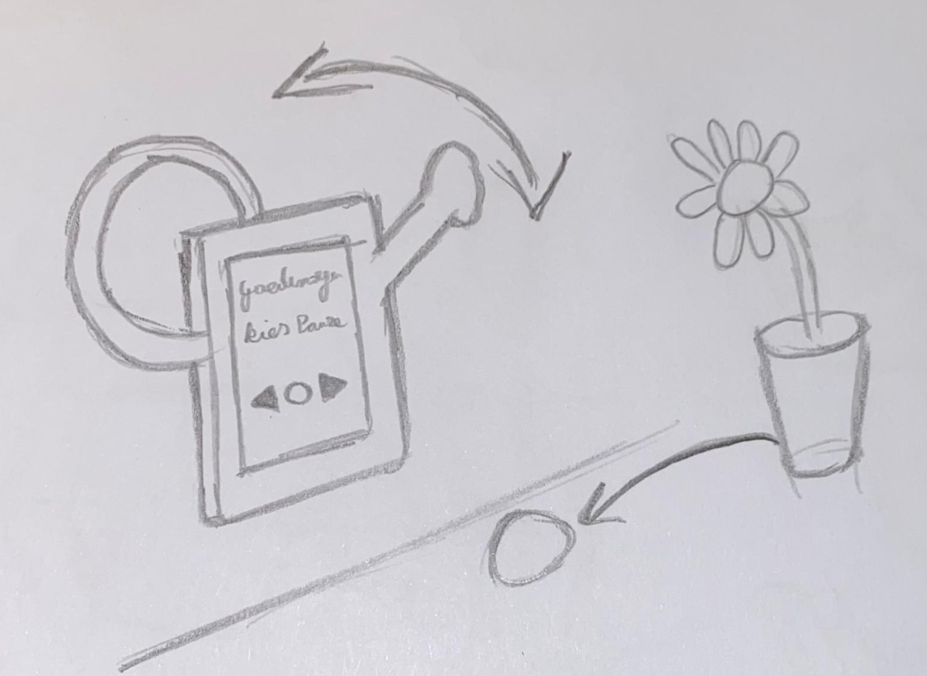
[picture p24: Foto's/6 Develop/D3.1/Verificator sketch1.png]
| Verificator | |

#### Roleplay

Voorafgaand aan het fysieke prototypen werd gekozen om te werken met roleplay. Deze methode maakt het mogelijk om in een vroeg stadium de gebruikerservaring visueel uit te denken en eerste gebruiksfouten of knelpunten te detecteren, zonder reeds te investeren in complexe of tijdrovende prototypes.

De elementen die gebruikt worden voor de roleplay konden snel verwezelijkt worden door zaken zoals bijvoorbeeld een drinkfles met post-its op geplakt. Dit gaf een eerste inzicht in hoe het systeem zich gedraagt in verschillende scenario’s op de werkvloer. Dit hielp bij het afstemmen van verwachtingen met stakeholders en bood een duidelijke basis voor de verdere ontwikkeling van functionele prototypes. 

Op onderstaande afbeeldingen is te zien hoe het concept van een bloem als feedbackunit is gerealiseerd met drinkflessen met verschillende kleuren post-its. Deze verschillende kleuren representeren de status van de bloem (slap of rechtopstaand). De verificator in de vorm van een gieter werd getekend op papier en opgehangen aan de muur. Met deze componenten kon al een eerste roleplay als volgt van start gaan:

De verpleegkundige (in dit geval Pieter) doet zijn verpleegkundige taken ergens op de afdeling. Vervolgens voelt hij de wearable die hij draagt trillen en ziet hij dat de bloem op de verpleegkar volledig slap hangt, nu weet hij dat het tijd is om even wat rustiger aan te doen en misschien even een korte pauze te nemen. Daarom neemt hij de bloem van de zorgkar en gaat hij ermee naar de verificator die zich bevind in de verpleegpost. Vervolgens plaats hij de bloem op de voorziene plaats bij de verificator en kiest hij een pauzeopdracht die hij graag wil doen. Nadat de pauze is afgelopen neemt hij de bloem terug mee naar de verpleegkar en hervat hij zijn werk.

<p align="center">
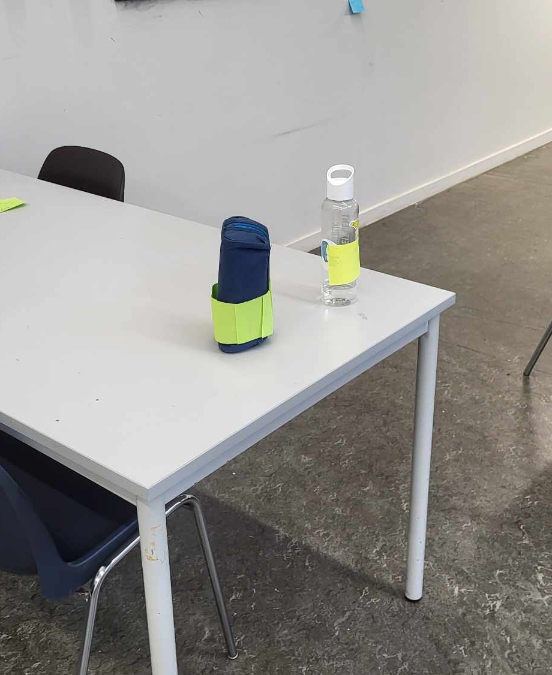
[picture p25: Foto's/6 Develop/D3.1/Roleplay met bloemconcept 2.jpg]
  
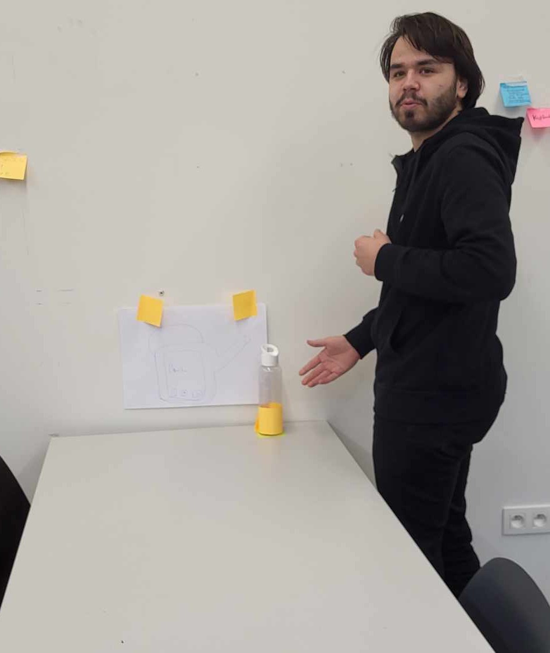
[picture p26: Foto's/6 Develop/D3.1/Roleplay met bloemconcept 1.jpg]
  
</p>

Uit deze roleplay zijn verschillende aandachtspunten tevoorschijn gekomen:
- De bloem moet uitgerust worden met een lampje dat van kleur veranderd om onderscheid te kunnen maken van een bloem die nog net niet helemaal slap hangt vs een bloem die wel volledig slap hangt.
- Men kan makkelijk de bloem vergeten mee te nemen wat het onmogelijk maakt om in te loggen op de verificator. Dit kan ook als een overbodige taak gezien worden.

#### Prototyping
Het doel van dit prototypingproces was om een algemeen concept te kunnen valideren om dit vervolgens in een volgend onderdeel te kunnen verfijnen. Het prototype voor stressfeedback, zal in de concepttest geëvaluereerd worden op begrijpelijkheid, impact en bruikbaarheid binnen de context van woonzorgcentra. De bedoeling was om na te gaan op welke manier er feedback op een betekenisvoll gecommuniceerd kan worden, zonder de werkomgeving of collega’s te storen.
Omdat er op dit moment nog geen concept vast ligt en omdat het project een grote omvang heeft gezien de verschillende componenten, was het moeilijk om aan varity prototyping te doen. De gemaakte prototypes worden in onderstaande tabel weergegeven en de werking wordt ervan besproken.

| Prototype      | Beschrijving                                                                                                                                 |
|----------------|----------------------------------------------------------------------------------------------------------------------------------------------|
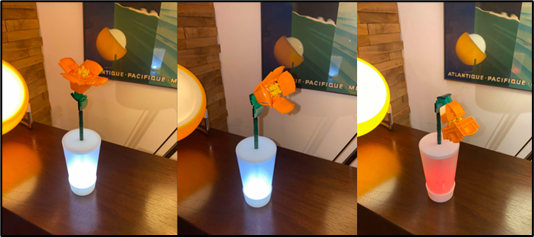
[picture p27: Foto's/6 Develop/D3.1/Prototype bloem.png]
|  | **Feedback unit (hoofdfocus):**<br>Elke gebruiker heeft een eigen bloem op zijn/haar zorgkar staan. De bloem gaat slapper hangen naarmate het stressniveau toeneemt.<br><br>Zodra de bloem volledig slap hangt, zal de kleur van de bloempot rood kleuren. Op dat moment is het tijd om de bloem water te geven → pauze nemen. |
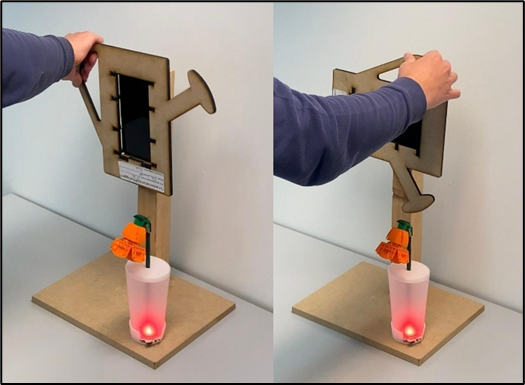
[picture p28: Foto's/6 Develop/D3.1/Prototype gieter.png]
|  | **Verificator (gieter):**<br>Wanneer de bloem aangeeft dat het tijd is voor een pauze (door slap te hangen en een rode pot te tonen), moet deze bij de **verificator (gieter)** worden geplaatst.<br><br>De verificator herkent de eigenaar van de bloem en stelt verschillende pauzes voor. De gebruiker kiest een pauze, waarna de verificator de starttijd registreert. Kort voor het einde van de pauze trilt de wearable om aan te geven dat het tijd is om het werk te hervatten.<br><br>Hierbij moet de gebruiker de pauze met een knop op de verificator stoppen. Indien de pauze goed is uitgevoerd, heeft men water verdiend om de bloem weer gezond te maken (bloem rechtop en pot kleurt groen). |
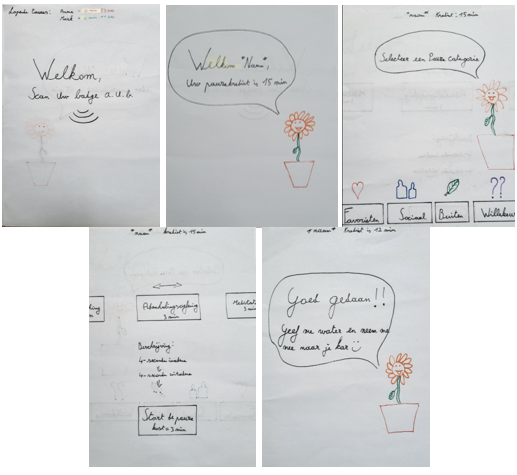
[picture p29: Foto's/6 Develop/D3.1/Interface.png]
| |  De verificator bevat een **interface** die de gebruiker verschillende pauzes kan voorstellen. Tegelijk is dit een systeem dat de pauzes zal loggen om misbruik zoveel mogelijk tegen te gaan. |

#### User testing 
De voorgaande methodes zoals roleplaying, brainstorming, prototyping,... hebben doorheen het proces geleid tot verschillende ontwerpvragen te zien in [Protocol develop 3.1](https://github.com/DePieter/TakeFive/blob/main/Protocols/Develop/Test%20protocol%203.1.pdf). Om deze ontwerpvragen te beantwoorden, werd een gebruikerstest uitgevoerd waarbij het concept werd voorgesteld en vervolgens werd gevraagd om in de context intuïtief te interageren met het systeem. De respondenten werden verkregen door telefonisch contact op te nemen met WZC Panhuys Gent. Aangezien er met deelnemers werd gewerkt, ondertekende elke deelnemer een ‘informed consent’, terug te vinden in de bijlagen.
De concepttest heeft als doel antwoord te krijgen op volgende ontwerpvragen:     
  
**Conceptuele validatie (Definition-fase)**
- In welke mate sluit de voorgestelde pauzestrategie aan bij de noden en verwachtingen van zorgmedewerkers? (=wat is de opinie van de gebruiker)?
- Hoe betrouwbaar en consistent functioneert het systeem onder verschillende werkomstandigheden en stressniveaus?
- Welke drempels ervaren gebruikers bij het gebruik van het systeem, en hoe kunnen deze worden verminderd?
- Is een verificator (zie Prototypes) noodzakelijk, of volstaat het als de feedbackunit zelf aangeeft welke pauze genomen moet worden, bijvoorbeeld via een geïntegreerd display?
- Kan het systeem omzeild worden (bv. te weinig of te veel pauze nemen) en hoe kan dit e.v.t. worden opgelost?

**Ergonomische aspecten (Development-fase)**
- Hoe intuïtief en toegankelijk is de interactie met het systeem voor zorgmedewerkers in een veeleisende werkomgeving?
- Welke vorm/uiterlijk van de feedback unit biedt de beste sensoriele ergonomie aan de gebruiker?
- Hoe beïnvloedt dit systeem de cognitieve belasting en werkprestaties?
- Worden de meldingen en suggesties van het systeem als helpend of storend ervaren tijdens het werk?
- Hoe goed past het systeem binnen de bestaande workflow van zorgmedewerkers zonder extra stress of werkdruk te veroorzaken?

De geanalyseerde data wordt vertaald naar antwoorden op de ontwerpvragen, wat leidt tot verschillende design requirements. Deze zaken zijn terug te vinden in [Rapport develop 3.1](https://github.com/DePieter/TakeFive/blob/main/Reports/Develop/Concept%20test%20rapport%203.1.pdf).

#### MoSCoW
Om alle verkregen data (concepttest, opmerkingen van roleplay,...) op een structurele manier te verwerken, werd d.m.v. een extra uitgebreide MoSCoW- methode in combinatie met brainstorming, een waardevolle tabel bekomen welke resulteert in concrete ontwerpvragen, design requirements en aandachtspunten.
In deze MoSCoW-tabel heeft elk teamlid zoveel mogelijk relevante vragen geformuleerd welke voortvloeien uit reeds uitgevoerde methoden. Vervolgens zijn deze gezamenlijk besproken en beoordeeld, wat heeft geleid tot waardevolle discussies en oplossingen. Desbetreffende tabel wordt hieronder weergegeven:

| Nr. | Vraag | Ontwerpimplicatie | MoSCoW | Opmerkingen/Oplossing |
|-----|-------|-------------------|--------|------------------------|
| 1 | Mag de gebruiker pauze nemen? | Er moet heel duidelijk gesignaleerd worden naar de gebruiker dat deze pauze mag nemen om verwarring te vermijden. | M | Eénduidige signalisatie |
| 2 | Neemt de gebruiker niet te lang pauze? | Er moet een manier zijn waarop deze op de hoogte wordt gebracht wanneer de pauze voorbij is. | M | Vlak voor afloop moet de wearable beginnen trillen, tot dat de pauze wordt beëindigd met de stopknop op de verificator. <br> & <br> Hoofdverpleegkundige/afdelingshoofd moet de beschikbare pauze kunnen regelen. |
| 3 | Kan er worden nagegaan dat de pauze effectief wordt genomen? | Het moet duidelijk zijn naar de gebruiker en anderen toe dat de pauze moet worden genomen. <br><br> Ook moet er een controlemiddel zijn op technologisch vlak. De gebruiker moet verifiëren dat deze de pauze neemt. | M | Bloem eventueel op slot bij nemen van pauze. <br> Bij start van pauze start een timer, zorg dat andere VPK de lopende timers ook kunnen zien (sociaal stigma). <br> Bij einde van pauze moet nog eens op een knop gedrukt worden. <br> Werken zonder bloem sociaal onaanvaard. |
| 4 | Kan er op worden valsgespeeld? | / | / | Dit zal de test moeten uitwijzen |
| 5 | Moet de pauzeopdracht worden voorgesteld door de feedbackunit? | Het is geen vereiste om in elke kar een unit te integreren met scherm en interface (kostprijs). | M | Psychologisch worden ruimtes gekoppeld aan handelingen. Om doorwerken te vermijden, wordt gebruiker verplicht naar pauzeruimte te gaan. Verificator (= gieter) in pauzeruimte plaatsen. |
| 6 | Wat kunnen we met de data uit de wearable? | Een app/interface voor afdelingshoofden kan meerwaarde bieden | S | Taakverdeling regelen, life-inzichten geven van medewerkers |
| 6.1 | Moet de gieter een functie bieden om de gevoeligheid van het systeem te beperken? | Zie vraag 2 | M | Zie vraag 2 |
| 7 | Welke ruimte is het meest geschikt voor de verificator? | Geeft inzicht over de beste plaatsen. | / | De pauzeruimte -> zie vraag 5 |
| 8 | Welke manier van interactie wordt verkozen door de gebruiker? | Is een fysieke interface beter (bv knoppen) of volstaat een digitale aanpak? | / | Enkel de verificator krijgt display + knoppen. Focus ligt op de feedbackunit (=bloem). |
| 9 | Hoe kunnen we de gebruiker verwittigen dat de pauze voorbij is? | / | M | De wearable moet een trilsignaal geven. |
| 10 | Bestaan er gelijkaardige concepten? | Heuristiek met bestaand fenomeen? | / | [Little Signals](https://littlesignals.withgoogle.com/) <br> [TouchPoint](https://thetouchpointsolution.com/pages/emdr) <br> [Soft Robot Design](https://elenasabinson.com/soft-robot-system-design) |
| 11 | Hoe kunnen we de feedbackunit antropomorferen? | Werken met een “buddy” is vaak aangenamer en motiverend. | S | Concept bevat een bloem die slap hangt bij toenemend stressniveau. |
| 12 | Wanneer mag de feedbackunit veranderen van status? | Stressniveau verschilt per persoon. | M | Eerste week enkel metingen. Daarna systeem activeren. Vervolgens passief blijven analyseren en bijsturen. |
| 12.1 | Hoe omgaan met ongewenste meldingen? | Wanneer in slaapstand? | M | Feedbackunit gaat in slaapstand bij uitdoen van wearable. |
| 14 | Hoe worden opdrachten gekoppeld aan de verificator? | Buitenopdrachten vragen specifieke plaatsing. | S | Meerdere verificators: <br> • Buitenopdrachten: bij uitgang. <br> • Binnenopdrachten: in pauzeruimte. |
| 15 | Is een dockingstation nodig? | / | S | Extra esthetische waarde (bv bloembak). <br> Wearable & FU kunnen daar opgeladen worden. |
| 15.1 | Wat als opladen vergeten is? | Uitwisselbare reservebatterij. | C | / |
| 16 | Kan het oplaadpunt en verificator samen worden gebracht? | / | / | Via oplaadstation bij verificator. <br> Micro-interactie: “aan het opladen”-signaal via groen pulserend licht. |
| 17 | Is een deelsysteem mogelijk? | Aan gebruiker vragen. | W | Moeilijk door shiften en batterijniveau. |
| 18 | Moet back-end rekening houden met duur pauze? | / | M | Pauze wordt gestuurd door hoofdverpleegkundige (zie vraag 2). |
| 19 | Hoe lang duurt interactie met verificator? Kans op dubbele bezetting? | Interactie moet kort zijn. | M | Snel en toegankelijk. Minimale wachttijd. |
| 20 | Hoe gebruiksvriendelijk is het product? | Between-subjects test. | M | Groep 1 krijgt uitleg, groep 2 test intuïtief. |
| 21 | Kan er mechanisch valsgespeeld worden? | Betrouwbare bloemknop nodig. | M | Stevige mechanische scharnier + lichtkleur voor status. |
| 22 | Wil elke zorgmedewerker het product gebruiken? | Alternatief indien iemand geen pauze wil/mag nemen. | / | Geen verandering, verantwoordelijkheid bij gebruiker. |
| 23 | Moet het product slimmer zijn dan de gebruiker? | Kijken naar manipulatie & relevantie. | / | / |
| 26 | Hoe start interactie met verificator? | Stations of interface? | M | Te testen: badge scanner / wearable scan / bloem scan. |
| 27 | Moet het product gebruiker detecteren? | Nabijheidsdetectie vermijden onnodige interactie. | W | / |
| 28 | Wat doen met data buiten pauzes? | Value promise uitbreiden. | S | Webapp met stressoverzicht, taakvariatie aanduiden. |
| 29 | Hoeveel is te veel? | Moet alles wat bedacht is, er effectief in? | C | Data: volledige toegang optioneel voor hoofdverpleegkundige. <br> Prototypes bepalen wat nodig blijkt. |
| 30 | In hoeverre wil men privacy? | Hoeveel data mag gekend zijn door collega’s? | S | Hoofdverpleegkundige als vertrouwenspersoon. |
| 31 | Hoe batterijstatus weergeven? | / | M | Op FU zoals JBL speaker. Verificator met lichtsignaal (zie vraag 16). |
| 32 | Moet feedbackunit mee naar verificator? | Verificatie via wearable. | M | Testen. <br> Kan vervangen worden door badge-scan of naamselectie. (zie vraag 26) |
| 33 | Wordt pauze als extra gezien? | Hoe wordt deze geïmplementeerd? | M | Hoofdverpleegkundige kan pauzekrediet bepalen. |

#### Conclusies & implicaties
Het doel van deze fase was tweeledig; eenderzijds was het de bedoeling om een algemeen concept te kunnen valideren en anderzijds was het de bedoeling om al enkele eerste stappen te zetten richting de optimalisatie omtrend de ergonomie. 
Concreet zijn de belangrijkste hoofdzaken die voortvloeien uit deze wave als volgt:
- Dergelijk systeem wordt gewaardeerd door het zorgpersoneel.
   >_"Ik ervaar veel stress tijdens het werk. Een extern apparaat dat mij eraan herinnert om een pauze te nemen op basis van mijn stressniveau zou ik erg appreciëren." -Jonatan (verpleegkundige WZC Panhuys)_
- De feedbackunit in zijn huidige vorm als bloem, zorgt voor een negatief stigma.
   >_“Als iemand mij vertelt dat er 8 bloemen slaphangen, zwier ik ze buiten.” -Laurence (zorgkundige WZC Panhuys)_
- De feedbackunit mag niet op de zorg kar staan aangezien deze locatie te zichtbaar is.
   >_“Als ik veel stress heb wil ik dit niet open en bloot tonen, zeker niet als ik bij mijn patiënten ben of als er famillie op bezoek is.” -Sofie (zorgkundige WZC Panhuys)_
- Om de focus op alle 3 de componenten (wearable, feedbackunit, verificator) te leggen, gaat het een grote uitdaging worden om alles binnen de deadline van dit project te leggen. Daarom wordt vanaf nu de hoofdfocus gelegd op enkel de feedbackunit.

Als conclusie zijn er verschillende designrequirements opgesteld die in acht genomen moeten worden voor het verder opbouwen van het concept, deze zijn hieronder te zien:
Dit proces resulteerde in concrete ontwerpvragen, design requirements en aandachtspunten voor de concepttests. 

| ID    | Design Requirements                                                                                                                    | Source    | Date       |
|-------|----------------------------------------------------------------------------------------------------------------------------------------|-----------|------------|
| DR26  | De feedback unit moet discreet zijn en enkel interpreteerbaar voor collega’s. Dit door te werken met visuele Affordances.             | Test&nbsp;3.1  | 24/02/2024 |
| DR27  | Gebruikers moeten zelf kunnen kiezen wanneer ze hun pauze nemen.                                                                       | Test 3.1  | 24/02/2024 |
| DR28  | De feedback unit moet individueel herkenbaar zijn en niet gelinkt aan een gedeelde zorgkar.                                            | Test 3.1  | 24/02/2024 |
| DR29  | De wearable moet minimale verstoring veroorzaken en niet te vaak trillen.                                                              | Test 3.1  | 24/02/2024 |
| DR30  | De verificator moet zich dichtbij bevinden om de drempel tot pauzes te verlagen.                                                       | Test 3.1  | 24/02/2024 |
| DR31  | Het systeem mag geen extra werkdruk of cognitieve belasting veroorzaken.                                                                | Test 3.1  | 24/02/2024 |
| DR32  | Een snooze-functie moet mogelijk zijn om pauzes uit te stellen.                                                                         | Test 3.1  | 24/02/2024 |
| DR33  | Het systeem moet een positieve stimulans bieden, zoals kleine gelukjes, om acceptatie te verhogen.                                     | Test 3.1  | 24/02/2024 |
| DR34  | Het systeem moet rekening houden met piekmomenten (ochtend- en avondzorgen) bij pauzevoorstellen.                                      | Test 3.1  | 24/02/2024 |

**Te testen:** 
- Kan er valsgespeeld worden met de pauze-verificatie? 
- Wat is de meest efficiënte manier om interactie met de verificator te starten? (Badge, wearable, bloem) 
- Hoe lang duurt de interactie met de verificator en zijn er wachttijdproblemen? 
- Wordt het als sociaal onaanvaardbaar gezien om zonder de bloem te werken? 
- Is het nodig om de feedbackunit fysiek mee te nemen naar de verificator, of is een alternatieve verificatiemethode beter? 
- Gebruikerservaring testen: intuïtief gebruik vs. uitleg krijgen. 

---
### Develop 3.2 [Affectief ontwerp]:  
>_“Zorgen voor begint bij goede zelfzorg.” -Stijn (Directeur WZC Sint-Franciscus)_
#### Doelstellingen (cfr. methodologie)
Uit de vorige test bleek dat het concept — een combinatie van een wearable, feedbackunit en verificator — bruikbaar is. Tegelijkertijd werd duidelijk dat de huidige vorm van de feedbackunit, een bloem, een negatief stigma oproept en dus niet geschikt is. In deze fase wordt daarom onderzocht welke metafoor beter past voor de feedbackunit. Daarnaast is het belangrijk te achterhalen welk gevoel deze metafoor idealiter moet oproepen: moet deze motiveren om harder te werken, of net rust brengen in stressvolle momenten?

#### Materiaal en methoden (N = 5)
Voorgaande fase heeft aangetoond hoe de feedbackunit moet functioneren en welke kernkwaliteiten essentieel zijn. Nu is het cruciaal om de meest geschikte metafoor te vinden, dit om op gepaste wijze de juiste emoties op te roepen. Om tot de beste keuze te komen, worden methoden ingezet voor het achterhalen van betekenisvolle en contextgevoelige metaforen. Zo wordt via antroposemiotiek onderzocht hoe zorgverleners betekenis geven aan vormen en bewegingen. Emotional mapping wordt ingezet om emotionele reacties op verschillende metaforen in kaart te brengen. Daarnaast zorgt A/B-testing ervoor dat concrete ontwerpvarianten systematisch worden vergeleken. Het complete protocol van de test die is uitgevoerd in deze fase, is te raadplegen via: [Protocol develop 3.2](https://github.com/DePieter/TakeFive/blob/main/Protocols/Develop/Test%20protocol%203.2.pdf) 

#### Brainstorming
Om tot geschikte metaforen voor de feedbackunit te komen, werd met het team een gerichte brainstormsessie georganiseerd. Het doel was om ideeën te creëren die zowel emotioneel resoneren met zorgmedewerkers als functioneel bruikbaar zijn op een feedbackunit in een zorgomgeving.

Er werd gestart met een korte reflectie over hoe de huidige feedbackunit (de bloem) een onbedoeld negatief stigma opriep. Daarna volgde een individuele ideefase waarin elk teamlid op post-its zoveel mogelijk metaforen noteerde die gevoelens oproepen zoals rust, zorg, verbondenheid en vreugde. Deze ideeën werden vervolgens gebundeld, besproken en geclusterd op thematiek.

In deze brainstormsessie werd er gebruik gemaakt van verschillende methodieken:

- Metaphor Cards: er werden post-its gemaakt met verschillende zaken op die kunnen dienen als metafoor voor de feedbackunit zoals bv koffietas, zon, mist,...

- Verhalenmethodiek: elk teamlid bracht situaties aan waarin zorgverleners mogelijk overprikkeld raken of net tot rust komen, en beschreef hierbij wat in die situaties visueel of emotioneel opviel.

- Thema-associaties: de metaforen zullen gekoppeld worden aan concepten zoals zelfzorg, teamgevoel en herstel.

<div align="center">
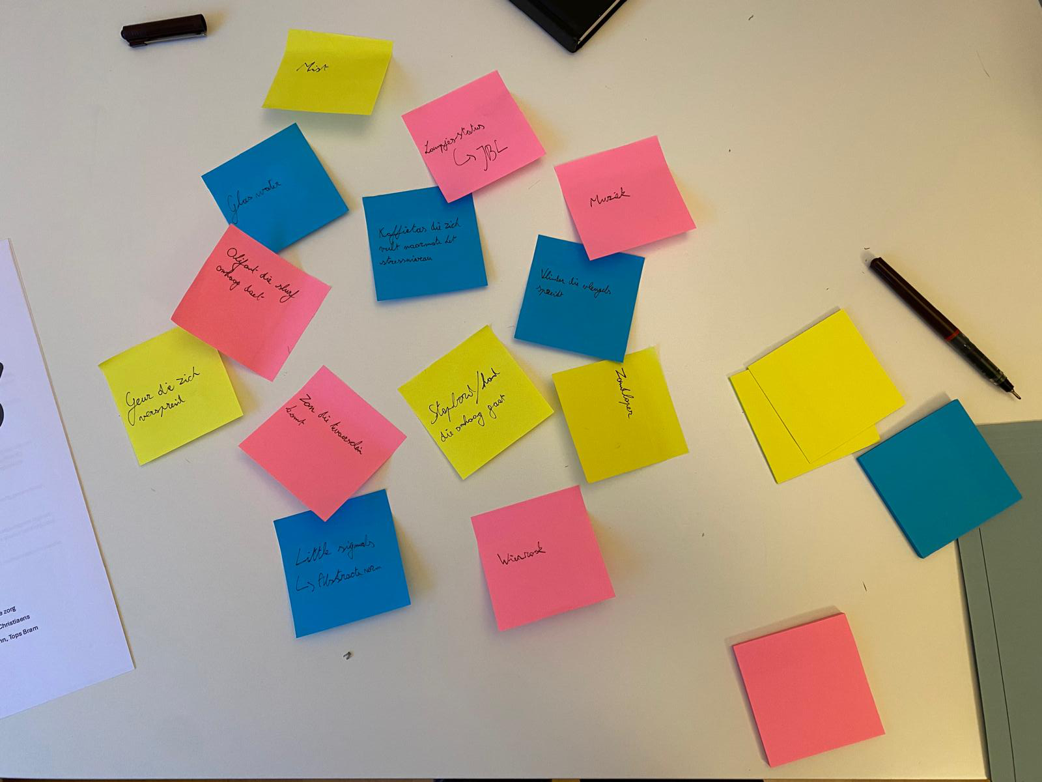
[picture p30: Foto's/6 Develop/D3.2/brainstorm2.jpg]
  
</div>

Als resultaat van deze brainstormsessie, kan er gezegd worden dat alle afbeeldingen die op een manier rust uitstralen interessant kunnen zijn. Wat de metafoor precies zou moeten zijn is nog vrij vaag, wat het antwoord precies is op deze vraag zal moeten blijken uit een test.

#### Prototyping
Het prototype is ontwikkeld om te onderzoeken hoe zorgmedewerkers discrete signalen waarnemen en welke voorkeuren zij daarbij hebben. Voor het ontwerp diende 'Little Signals' van Google als inspiratie, omdat dit concept op een subtiele manier signalen vormgeeft.
Het prototype (zie onderstaande foto) bevat drie verschillende actuatoren, die elk een ander type beweging en communicatievorm simuleren. Ze worden handmatig bediend via de achterkant:

-	Cilinder 		->  abstracte vorm
-	Op- en neergaande foto	->  beeldje in de vorm van een metafoor
-	Bewegend papier		->  Golvende beweging
-	Gsm-scherm		->  [Bewegend licht](https://github.com/DePieter/TakeFive/blob/main/src/golvende%20beweging.mp4)

<div align="center">
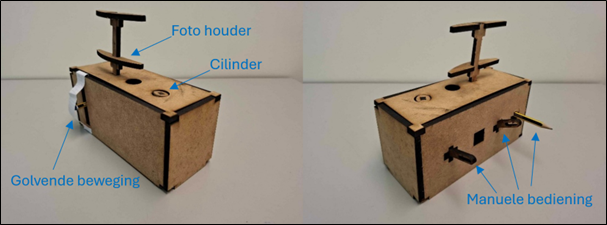
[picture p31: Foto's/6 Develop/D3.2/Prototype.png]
  
</div>

#### Emotional mapping
Plutchiks Wheel of Emotions is een model dat helpt om emoties in kaart te brengen, het bevat acht emoties: vreugde, vertrouwen, woede,... Zo wordt het eenvoudiger voor de woonzorgmedewerkers om de metaforen aan emoties toe te wijzen. Hierdoor kunnen de juiste metaforen gekozen worden voor de FU.

#### User Testing (n=5)
Tijdens deze testfase werd het prototype (Wizard of Oz, 3-in-1) getoond aan vijf zorgverleners. Hierbij werd onderzocht hoe zorgverleners emotioneel reageren op verschillende metaforen en bewegingen. De test startte met het tonen van de drie actuatoren van het prototype, gevolgd door papieren afbeeldingen van de bijhorende metaforen. De respondenten plaatsten deze op Plutchiks Wheel of Emotions. Zo kon visueel worden vastgelegd welke emotionele respons elke metafoor opriep.

Deze techniek — het koppelen van gevoelens aan visuele metaforen via het emotiespectrum — bood niet alleen inzicht in de emotionele impact van elke metafoor, maar hielp ook om op een meer intuïtieve manier over gevoelens te praten. Doordat het wiel een gezamenlijke, visuele referentie bood, konden deelnemers makkelijker aangeven wat een bepaalde metafoor bij hen opriep, zoals rust, afkeer of vreugde. Tegelijkertijd werd de onderliggende betekenis van vormen, kleuren en bewegingen bevraagd aan de hand van doelgerichte vragen.

Het doel was om duidelijk te achterhalen welk gevoel het systeem idealiter moet oproepen, en welke combinatie van metafoor en beweging dat gevoel het best vertegenwoordigt. Bijvoorbeeld: roept een zacht bewegende vlinder eerder rust of verdriet op? En welk gevoel roept een ritmisch op- en neergaande koffietas op?

Deze testmethode hielp zo niet alleen om feedback te verzamelen, maar legde ook verbanden tussen vorm, beweging, emotie en betekenis in de zorgcontext.

<p align="center">
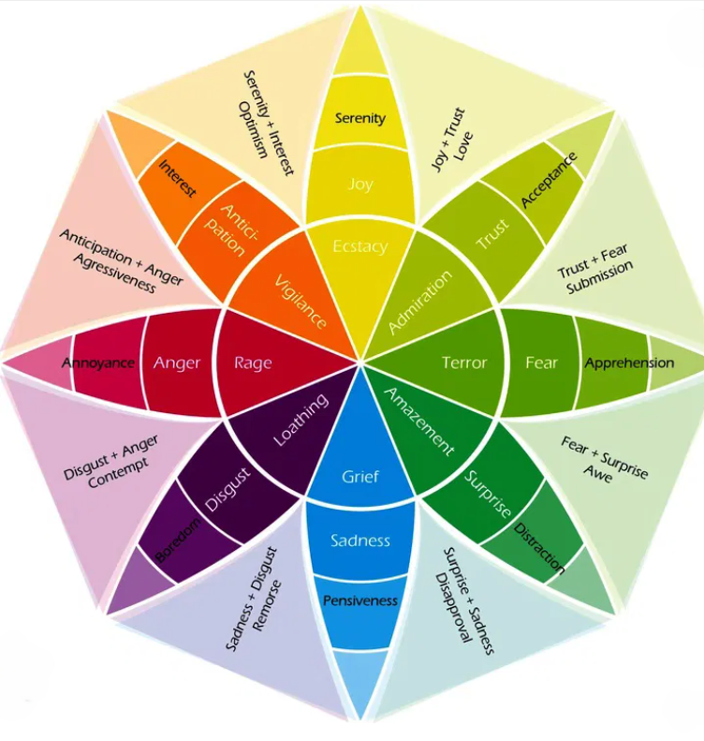
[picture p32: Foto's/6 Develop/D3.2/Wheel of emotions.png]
  
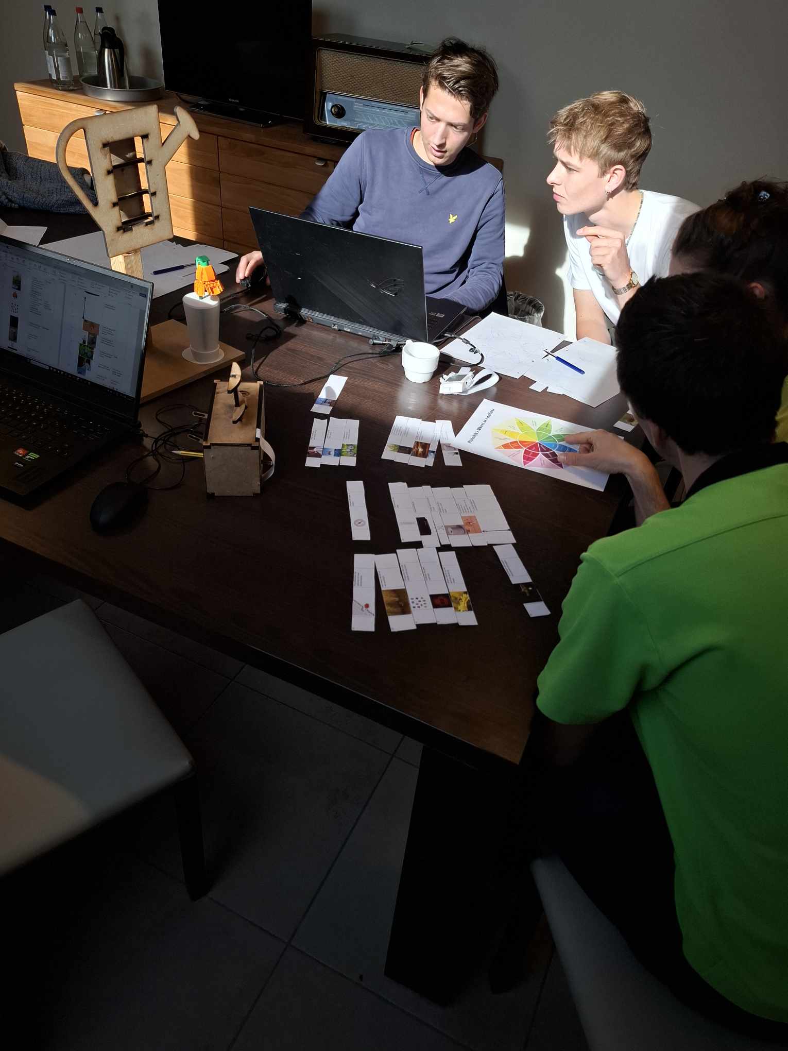
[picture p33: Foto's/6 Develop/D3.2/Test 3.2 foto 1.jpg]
  
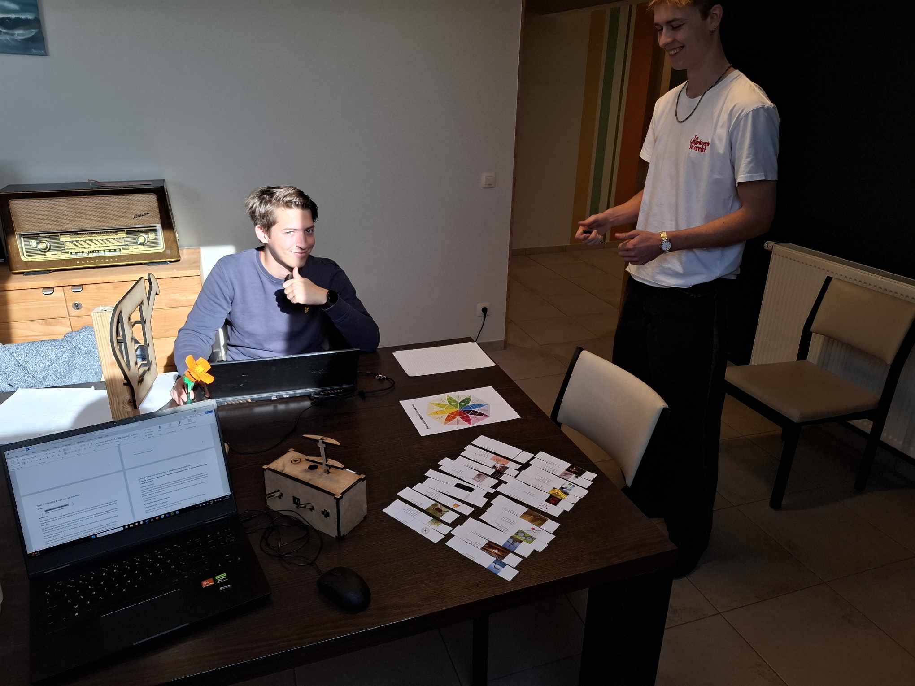
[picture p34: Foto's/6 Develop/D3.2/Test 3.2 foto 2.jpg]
  
</p>
  
#### Resultaten
Deze test heeft veel waardevolle inzichten opgeleverd, zo toonde de [raw data](Raw%20Data/Develop/Develop%203.2) aan dat metaforen (voornamelijk dieren) die gevoelens van joy en rust oproepen het meest effectief en gewenst zijn. Deze gevoelens dragen volgens de respondenten positief bij aan het minderen van stress.
>_“Potverdorie de FU, staat weer beneden!” -Hilde (Verpleegkundige WZC Sint-Franciscus)_

Aan de andere kant werden metaforen zoals tandwielen en handen geassocieerd met negatieve emoties zoals woede en frustratie: “Je blijft maar bezig”, wat zorgmedewerkers kan frustreren.
>_“De koffietas als metafoor vind ik heel leuk en toepasselijk!” -Bruno (Ergotherapeut WZC Sint-Franciscus)_

Wat betreft de beweging van de metafoor, gaf de meerderheid van de respondenten aan dat de beweging het best gekoppeld zou moeten zijn aan de gebruikte metafoor; als er een olifant wordt gebruikt als metafoor, zou de beweging logischerwijs een op en neergaande slurf kunnen representeren.

#### Conclusies & implicaties (design requirements en beslissingen)
Het systeem moet emoties oproepen die bijdragen aan een positieve, ondersteunende en ontspannen werkomgeving, waarin zorgmedewerkers zich veilig en persoonlijk betrokken voelen. De focus ligt op het stimuleren van gevoelens van vreugde en rust. Uit de test bleek dat vooral dierlijke metaforen het best scoorden. De gekozen beweging zal afgestemd worden op de gebruikte metafoor en moet daarmee een logisch en intuïtief verband vertonen. Deze fase heeft uiteindelijk geleid tot verschillende design requirements:

| ID    | Design Requirements                                                                                                                                                           | Source       | Date       |
|-------|--------------------------------------------------------------------------------------------------------------------------------------------------------------------------------|----------|------------|
| DR35   | De feedbackunit moet in de zorgpost staan.                                                                                                                                    | Test&nbsp;3.2 | 6/03/2025  |
| DR36   | De feedbackunit moet uiterst stevig en duurzaam zijn. Dit betekent dat het waterdicht is, bestand tegen stoten en honderden keren zonder schade kan worden laten vallen.     | Test 3.2 | 6/03/2025  |
| DR37   | De feedbackunit mag niet makkelijk verplaatsbaar zijn.                                                                                                                        | Test 3.2 | 6/03/2025  |
| DR38   | De feedbackunit moet gebruik maken van rustgevende signalen.                                                                                                                  | Test 3.2 | 6/03/2025  |
| DR39   | Er zouden dieren gebruikt moeten worden in het signaalgeven.                                                                                                                  | Test 3.2 | 6/03/2025  |
| DR40   | Iedereens manier van signaalgeven moet gekozen kunnen worden.                                                                                                                 | Test 3.2 | 6/03/2025  |
| DR41   | Het moet ook andere data verzamelen zoals bijv. een stappenteller.                                                                                                            | Test 3.2 | 6/03/2025  |
| DR42   | Voor het hele ‘ecosysteem’ ontwerpen, niet enkel zorgmedewerkers.                                                                                                             | Test 3.2 | 6/03/2025  |
| DR43   | Het moet snel controleerbaar zijn zonder fysiek naar een feedbackunit te moeten lopen.                                                                                        | Test 3.2 | 6/03/2025  |
| DR44  | Niet iedereen moet andermans stressniveau kunnen zien, enkel een groepsindicatie.                                                                                             | Test 3.2 | 6/03/2025  |
| DR45  | Het mag geen grote veranderingen (“Franse Revolutie”) veroorzaken, maar het moet wel waardevol zijn.                                                                          | Test 3.2 | 6/03/2025  |
| DR46  | De feedbackunit moet de mogelijkheid hebben om met verschillende metaforen te werken.                                                                                         | Test 3.2 | 6/03/2025  |
| DR47  | De gebruikte metafoor moet rustgevend zijn en een gevoel van joy opwekken.                                                                                                    | Test 3.2 | 6/03/2025  |

---
### Develop 4: [Cognitieve ergonomie]  
>_“In een grote instelling heb je afdelingen met tien tot twintig medewerkers. Daar moet je rekening mee houden in het design.” -Jan (Directeur WZC De Weister)_

#### Doelstellingen (cfr. methodologie)
Deze test bevindt zich in de develop-fase waar voornamelijk het ergonomische aspect wordt onderzocht. Hierbij ligt de primaire focus op de feedback unit en word er op cognitief vlak de duidelijkheid van de signalisatie onderzocht. 

#### Materiaal en methoden
Om inzicht te verkrijgen in welk abstractieniveau van dierlijke vormen de grootste duidelijkheid biedt, wordt gebruikgemaakt van card sorting. Hierbij rangschikken zorgverleners visuele kaarten met dieren op negen abstractieniveaus – van realistisch tot extreem abstract en op basis van herkenbaarheid en interpretatiegemak.

Daarnaast wordt via een combinatie van think aloud, A/B-testing en kwantitatieve analyse onderzocht hoe bewegende metaforen en het gebruik van lichtsignaal (zie [wave 2 DR19](#wave2n5)) worden waargenomen in de context van de verpleegpost. Zorgverleners observeren een prototype in twee scenario’s: (1) enkel beweging van het dier, en (2) beweging in combinatie met een geïntegreerd LED-signaal. Door hun spontane interpretaties te registreren, wordt het verschil in duidelijkheid tussen beide situaties meetbaar gemaakt. Het complete protocol van de test die is uitgevoerd in deze fase, is te raadplegen via: [Protocol develop 4](https://github.com/DePieter/TakeFive/blob/main/Protocols/Develop/Test%20protocol%204.1.pdf).

#### Brainstorming
Uit D3.2 bleek dat er een duidelijke voorkeur was voor dieren als metafoor voor de feedbackunit. Op basis hiervan werd een gerichte brainstormsessie opgezet volgens een vereenvoudigde SCAMPER-methode om ieders input evenwaardig te verzamelen. Elk teamlid werkte eerst individueel ideeën uit rond mogelijke dierlijke metaforen en hun gedragingen (substitute, combine, adapt, modify, etc.). Nadien werden de ideeën gegroepeerd, besproken en geëvalueerd op basis van hun communicatiekracht, herkenbaarheid en technische haalbaarheid. De verschillende opties werden visueel geschetst en geclusterd rond centrale thema’s. Tijdens de plenaire bespreking werden er duidelijke ontwerpcriteria geformuleerd, die nadien als design requirements zijn vastgelegd (aangeduid met oranje markeringen op de foto). Deze gestructureerde aanpak zorgde voor een goed onderbouwde keuze richting de verdere ontwikkeling.

<p align="center">
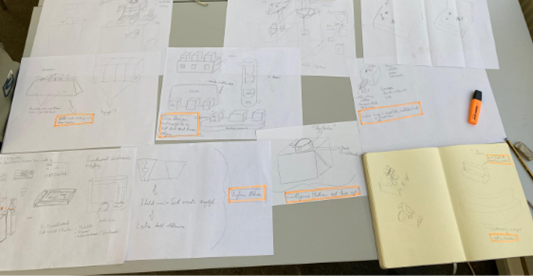
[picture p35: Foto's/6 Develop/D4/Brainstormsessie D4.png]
  
</p>

#### Prototyping
Uit voorgaande interpretatietest werd duidelijk dat een dierlijke metafoor een krachtig communicatiemiddel kan zijn binnen het systeem. Er werd een algemeen model gemaakt als FU dat gebruikt kan worden om verschillende soorten dieren per FU te integreren. Hierbij is ruimte voorzien om alle elektronica die nodig zou zijn om het dier te laten bewegen, in het model te verwerken. De LED-ring zal op het plateau bevestigd worden waar de dieren op kunnen staan. Er is beslist om de FU zodanig te ontworpen zodat er meerdere naast elkaar kunnen staan.

<p align="center">
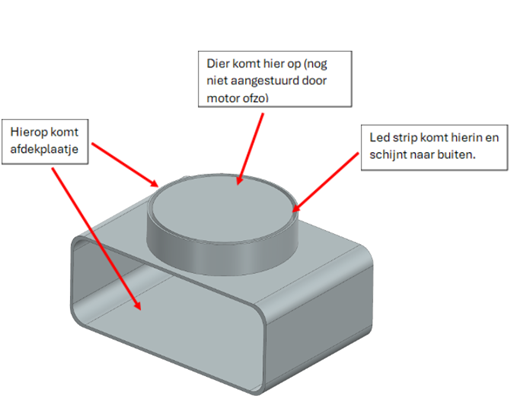
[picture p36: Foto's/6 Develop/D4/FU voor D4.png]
  
</p>

Uit de brainstormsessie zijn er 3 dieren gekomen waarvan een conceptuele beweging is bedacht om het stressniveau te representeren. Deze modellen (van [Printables](https://www.printables.com/model?ordering=views&period=month)) zullen in de volgende test deeld afgetoetst worden op het vlak van interpretatie door de gebruiker.

<table>
  <tr>
    <td>
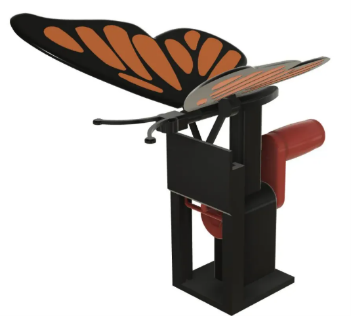
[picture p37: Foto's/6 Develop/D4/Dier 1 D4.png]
      
    </td>
    <td>
De vleugels van <strong>de vlinder</strong> zullen zich geleidelijk openslaan naarmate het stressniveau van de gebruiker stijgt. De vlinder is gekozen vanwege zijn uitstraling van lichtheid, vrijheid en lentegevoel.
    </td>
  </tr>

  <tr>
    <td>
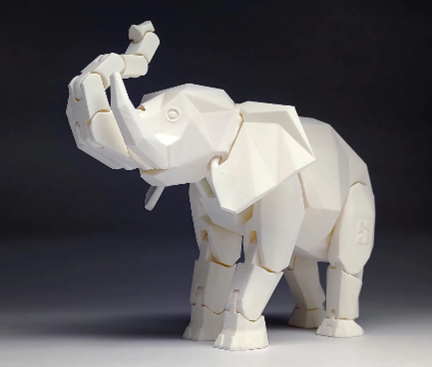
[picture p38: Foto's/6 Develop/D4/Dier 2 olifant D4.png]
      
    </td>
    <td>
De slurf van<strong> de olifant</strong> zal geleidelijk omhoog gaan naarmate het stressniveau van de gebruiker stijgt. De olifant is gekozen aangezien zijn uitstraling van kracht en stabiliteit.
    </td>
  </tr>

  <tr>
    <td>
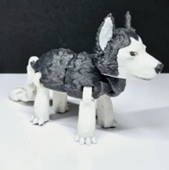
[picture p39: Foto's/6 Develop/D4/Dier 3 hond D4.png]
      
    </td>
    <td>
<strong>De hond</strong> ("Man's best friend") zal geleidelijk gaan zitten naarmate het stressniveau van de gebruiker stijgt. Dit dier werd gekozen als een goedgekend symbool van vertrouwen en rust.
    </td>
  </tr>
</table>

#### User Testing (n=5)
De test startte met een korte introductie waarbij het volledige project werd toegelicht. Na het invullen van een informed consent-formulier en het starten van een spraakopname, werd het doel van de test uitgelegd aan de hand van een herkenbaar voorbeeld zoals de ([Rorschachtest](https://nl.wikipedia.org/wiki/Rorschachtest)). Deze metafoor illustreerde het belang van interpretatie: bij de Rorschachtest ontstaat verwarring door té abstracte beelden, onderzoekt deze test net hoe ver een signaal geabstraheerd kan worden vóór het onherkenbaar wordt.

In de testsessie kregen de respondenten fotoreeksen te zien van verschillende dieren op negen verschillende [abstractieniveaus](#abstractieniveau) die liggen tussen: realistisch, gestileerd, geometrisch en extreem abstract, hieronder is daarvan een voorbeeld weergegeven:

<p align="center">
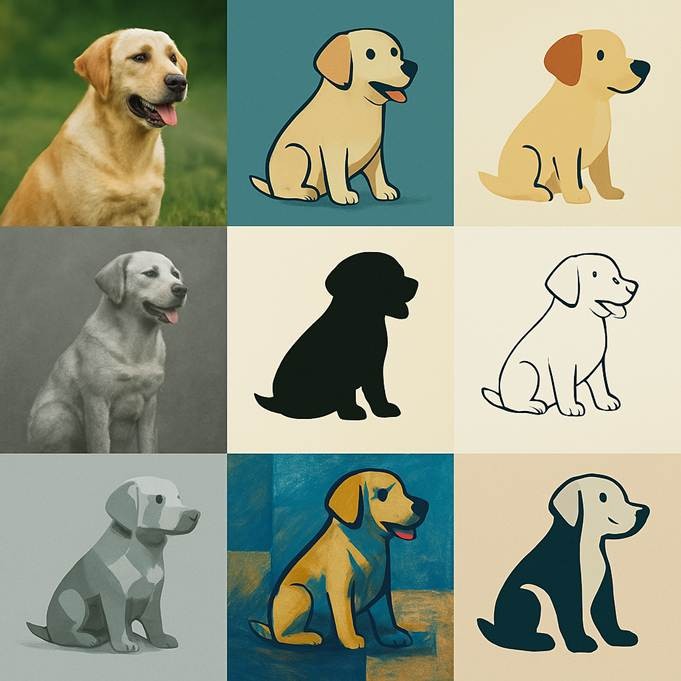
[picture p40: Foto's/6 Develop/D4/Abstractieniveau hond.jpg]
  
</p>

De opdracht bestond erin deze beelden te rangschikken van meest naar minst herkenbaar. De resulterende ordeningen werden per deelnemer vastgelegd via fotografie, met als doel een visuele en kwalitatieve analyse van voorkeuren en interpretatievermogen.

Daarna werd het prototype geïntroduceerd: een dierlijke metafoor met geïntegreerde lichtindicatie. In twee opeenvolgende scenario’s werd aan zorgverleners gevraagd wat zij waarnamen – eerst bij enkel beweging van het dier, vervolgens bij beweging in combinatie met licht. Door de reacties per situatie te vergelijken, was het de bedoeling om het verschil in duidelijkheid tussen beide condities kwantitatief vast te leggen.
Ten slotte werd er nog een korte vragenreeks afgelopen (terug te vinden bij [Protocol develop 4](https://github.com/DePieter/TakeFive/blob/main/Protocols/Develop/Test%20protocol%204.1.pdf)).

#### Resultaten
Uit de gesprekken met zorgprofessionals kwamen diverse waardevolle inzichten naar voren over de herkenbaarheid, interpretatie en vormgeving van dierlijke metaforen. Zo toonde de [raw data](Raw%20Data/Develop/Develop%204) duidelijk dat er een voorkeur bestaat voor abstractere beelden met een duidelijk contrast. Aan de andere kant mocht het er niet te kinderachtig uitzien door te veel kleuren en te simplistische cartoons.
>_“Het mag er niet kinderachtig uitzien.” -Jan (Directeur WZC De Weister)_

Daarbij is aan te geven dat kleurgebruik is toegestaan, mits het met zorg en in beperkte mate wordt toegepast.
>_“Kleuren geven snel duidelijkheid, maar een teveel eraan komt over als kinderachtig.” -Evy (zorgkundige: wonen en leven)_

Niet alle natuurlijke bewegingen van de dieren worden even positief waargenomen.
>_“Als de olifant zijn slurf omhoog doet, denk ik dat hij gaat aanvallen."_

De kwantitatieve test, waarbij deelnemers zo snel mogelijk moesten aangeven welke verandering ze aan de feedbackunit (FU) opmerkten, bleek weinig betrouwbaar. De reactiesnelheid varieerde sterk tussen de deelnemers: terwijl de ene deelnemer eerst rustig ging zitten en vroeg of hij al mocht beginnen, gaf een andere al antwoord na een eerste blik. Door deze inconsistente startmomenten en interpretaties is het niet mogelijk om op basis van deze test geldige uitspraken te doen over reactiesnelheid. De resultaten missen daardoor de noodzakelijke validiteit om als kwantitatieve data gebruikt te worden.

#### Conclusies & implicaties
De feedbackunit moet duidelijk en intuïtief communiceren, met een voorkeur voor abstracte dierfiguren en rustig kleurgebruik. Groen en warm wit zorgen voor rust, terwijl felle kleuren vaak als kinderachtig worden ervaren. Zonder uitleg is de functie niet altijd meteen duidelijk, wat de gewenste discretie weerspiegelt. Bewegingen en lichtsignalen gecombineerd bieden de beste herkenbaarheid.

De keuze van de beweging moet zorgvuldig gebeuren om een positief gevoel op te roepen. Uit eerdere tests blijkt dat de beweging logisch moet aansluiten bij het karakter van de gekozen metafoor. Uit deze test is gebleken dat ook de uitstraling van de beweging een belangrijke rol speelt: zo kan een olifant die zijn slurf omhoog steekt als bedreigend overkomen, terwijl een zittende olifant net een speelse en vriendelijke indruk wekt.

Op termijn is het de bedoeling dat elke gebruiker een eigen dier krijgt toegewezen, aangepast aan hun voorkeur, persoonlijkheid of teamdynamiek. Die personalisatie kan zich uiten in vorm, kleur of expressie. Voor het uiteindelijke uitwerken van een meer functioneel prototype, **zal er gefocust worden op één enkel dier**, zodat de werking en signaalduidelijkheid van de feedbackunit eerst in zijn eenvoud getest konden worden.

| ID    | Design Requirement                                                                                                                                | Source | Date       |
|-------|----------------------------------------------------------------------------------------------------------------------------------------------------|--------|------------|
| DR48  | De feedbackunit moet abstracte, niet-kinderachtige dierfiguren gebruiken om een professionele uitstraling te behouden.                            | Test&nbsp;4 | 03/04/2025 |
| DR49  | Bewegings- en lichtelementen moeten gecombineerd worden om duidelijke, begrijpelijke feedback te geven aan de gebruiker.                          | Test 4 | 03/04/2025 |
| DR50  | Het kleurgebruik moet rust en kalmte uitstralen, bijvoorbeeld door gebruik van warme wittinten of natuurlijke groentinten.                         | Test 4 | 03/04/2025 |
| DR51  | De betekenis van bewegingen moet intuïtief en positief geïnterpreteerd worden. Bewegingen met negatieve associaties (bv. angst) moeten vermeden worden. | Test 4 | 03/04/2025 |

---
### Develop 5: [Esthetische evaluatie & visuele test]
#### Doelstellingen
In dit onderdeel werd onderzocht hoe de Feedback Unit binnen het Take Five-systeem er visueel moet uitzien om optimaal te integreren in een zorgcontext (WZC en ziekenhuizen) rekeninghoudend met de cognitieve ergonomie en esthetiek. Het doel was om een ontwerp te ontwikkelen dat rust, vertrouwen en herkenning oproept bij zorgverleners.

#### Materiaal en methoden
Voor deze test werd een online enquête gelanceerd via Qualtrics (n = 35). Deelnemers kwamen uit verschillende leeftijdsgroepen en bestonden uit studenten, familie en kennissen. De volledige uitwerking kan worden teruggevonden in [Protocol develop 5.](https://github.com/DePieter/TakeFive/blob/main/Protocols/Develop/Concept%20test%20protocol%205.1.pdf)

Gebruikte testmethoden:

- **Moodboard (A/B) Test**  
  Deelnemers kozen welk moodboard het meest geschikt was voor een toestel in een zorgomgeving.  
  Resultaat: Moodboard 1 werd het meest passend ervaren.
  
  <p align="center">
  
</p>

- **Preference Test (Likert-schaal)**  
  Beoordeling van verschillende ontwerpvarianten op betrouwbaarheid (schaal 1–7).  
  Resultaat: Apparaat 1 scoorde het hoogst met een gemiddelde van 5.12.
  
<p align="center">
  
</p>

- **Desirability Test (woordkaarten)**  
  Deelnemers selecteerden 3 tot 5 woorden die het best pasten bij hun voorkeursontwerp.  
  Meest gekozen woorden: natuurlijk, kalmerend, vriendelijk.
  
- **5 Second Test**  
  Eerste indruk na het bekijken van een korte video van het prototype.  
  Veel deelnemers vonden het product visueel aantrekkelijk maar begrepen de functionaliteit niet direct, wat aansluit bij de wens voor een discreet ontwerp.
[![Bekijk video]](Foto's/6%20Develop/D5/beweging%20prototype.mp4)

#### Resultaten
De analyse voor de resulaten kan worden teruggevonden bij [Rapport develop 5.](https://github.com/DePieter/TakeFive/blob/main/Reports/Develop/Concept%20test%20rapport%205.1.pdf)
- Rustgevende kleuren (pastel- en aardetinten) en natuurlijke materialen (hout, stof) worden sterk geapprecieerd.
- Ronde vormen en zachte afwerkingen stralen vertrouwen uit.
- Abstracte diermetaforen, zoals een hond, worden positief ontvangen zolang ze niet kinderachtig overkomen.
- De visuele communicatie mag subtiel zijn. De functie hoeft niet meteen duidelijk te zijn voor bezoekers, zolang het personeel het begrijpt.

#### Conclusies & implicaties
De resultaten uit deze vijfde devellop bevestigen dat een rustige, natuurlijke esthetiek essentieel is voor een succesvolle integratie van de Feedback Unit in een zorgomgeving. De voorkeur gaat uit naar zachte vormen, warme materialen en discrete visuele communicatie. Deze inzichten vormen de basis voor verdere verfijning van het ontwerp in de eindfase van het project.
| ID   | Omschrijving                                                                 | Type | Bron    | Datum       |
|------|-------------------------------------------------------------------------------|------|---------|-------------|
| DR52 | Het ontwerp moet rust en vertrouwen uitstralen via ronde vormen              | M    | Test 5  | 17/05/2025  |
| DR53  | Gebruik van natuurlijke kleuren zoals pastel- of aardetinten                 | M    | Test 5  | 17/05/2025  |
| DR54  | Materialen moeten natuurlijk ogen, zoals hout en stof                        | S    | Test 5  | 17/05/2025  |
| DR55  | Afwerkingen mogen niet te glanzend of kil zijn                               | S    | Test 5  | 17/05/2025  |

## Conclusie  
### Slotbevindingen  
Ten einde van het projectvak Gebruiksgericht Ontwerpen, is een volledig concept ontwikkeld om stress bij zorgverleners de aandacht te geven die het verdient. Dit door de gebruikers meer bewust te maken van hun stressniveau. Het volledige poject is conceptueel uitbedacht en onderbouwd, waarbij een werkend prototype van de feedbackunit is ontwikkeld. Deze unit vormt samen met een draagbare sensor en een optionele verificator een compleet systeem dat zorgverleners helpt hun stressniveau tijdig af te bakenen.  

Het volledige concept is ondersteund door aangetoonde feiten en werd ontworpen met aandacht voor intuïtieve communicatie met de gebruiker, visuele en tactiele signalen en minimale afleiding tijdens het werk. Via een bewegend dier als metafoor en licht, geeft de FU directe maar discrete feedback over het gemeten stressniveau. Gebruikstesten met zorgverleners leverden waardevolle inzichten op voor de vormgeving en interactie, met als resultaat een toestel dat praktisch inzetbaar is en eenvoudig te integreren valt in het dagelijkse zorgproces.

Het project in dit stadium kan geklassificeerd worden als **TRL 6**, wat betekent dat het systeem in een relevante werkomgeving getest is en klaar is voor grootschaligere praktijktesten en verdere integratie in een volwaardig systeem. Daarbij wordt **geen rekening gehouden met de technische maturiteit van cortisolmetingen**, die op momenteel nog in ontwikkeling zijn. Het project vormt een concrete stap richting meer mentaal welzijn voor zorgpersoneel, met als doel het aantal burn-outs structureel te verminderen.

### Product design requirements
Doorheen dit volledige project zijn tijdens de uitgevoerde analyses (zoals PESTLE- en MoSCoW-analyse, plug & play testing, user interviews, user testing, ...) steeds meer design requirements vastgesteld. Deze helpen om het eindproduct zo goed mogelijk te omschrijven. In dit deel worden alle design requirements opgelijst per onderdeel van het eindproduct (wearable, verificator, feedbackunit). Het is daarbij belangrijk om opnieuw te benadrukken dat binnen het gebruiksgerichte onderzoek de meeste aandacht naar de feedbackunit is gegaan.

#### Algemeen
Hieronder staan de product design requirements voor de algemene werking van het product.
| ID   | Design Requirement                                                                 |  Source  | Date       |
|------|-----------------------------------------------------------------------------------|--------|------------|
| DR01 | Het ontwerp moet flexibel inspelen op wisselende personeelsbezetting gedurende de dag, zodat het inzetbaar blijft bij schommelingen in beschikbaarheid.   | Discovery |  /  |
| DR02 | Het systeem of de ruimte moet extra ondersteuning bieden tijdens piekmomenten, met name tijdens ochtend- en avondzorg, waarin de werkdruk het hoogst is.  | Discovery |  /  |
| DR03 | Het ontwerp moet flexibele pauzemomenten faciliteren, afgestemd op het actuele zorgritme, in plaats van vaste tijdsintervallen.                           | Discovery |  /  |
| DR05 | Het product moet inspelen op uiteenlopende gebruikerservaringen en zowel stressverlichting (pain relief) als positieve meerwaarde (value promise) bieden. | Discovery |  /  |
| DR08  | Het systeem moet de mogelijkheid bieden om de meldingsfrequentie en intensiteit te personaliseren, zodat gebruikers het kunnen afstemmen op hun voorkeuren en werkomstandigheden. | Wave 1       | 11/12/2024 |
| DR10  | Het systeem moet niet-invasieve meldingen bieden via visuele of tactiele signalen en storende functies zoals harde geluiden of buzzers vermijden. | Wave 1       | 11/12/2024 |
| DR14  | Prototypen moeten worden getest op gebruiksgemak en effectiviteit in een hectische zorgomgeving, met prioriteit voor eenvoudige bediening en snelle toegang tot kernfuncties. | Wave 1       | 11/12/2024 |
| DR15  | Er moeten verschillende methoden worden getest om gebruikers effectief te stimuleren pauzes te nemen, ook onder hoge werkdruk. | Wave 1       | 11/12/2024 |
| DR16  | Samenwerking met zorginstellingen is nodig om de stressmonitor te integreren in bestaande beleidskaders en het gebruik vrijwillig en breed toegankelijk te maken. | Wave 1       | 11/12/2024 |
| DR17  | Het ontwerp moet discreet en universeel toepasbaar zijn om stigma te minimaliseren en het gebruik als normaal en ondersteunend te positioneren. | Wave 1       | 11/12/2024 |
| DR18  | Het apparaat moet intuïtief en eenvoudig te bedienen zijn, met specifieke aandacht voor effectieve pauzemeldingen in drukke omgevingen. | Wave&nbsp;2       | 23/12/2024 |
| DR21  | Het apparaat mag lopende taken niet verstoren en moet eenvoudig in bestaande workflows passen. | Wave 2       | 23/12/2024 |
| DR23  | Het systeem moet modulair zijn, met instelbare meldingen en functies. | Wave 2       | 23/12/2024 |
| DR25  | Het ontwerp moet discreet en universeel toepasbaar zijn om stigma te verminderen. | Wave 2       | 23/12/2024 |
| DR27  | Gebruikers moeten zelf kunnen kiezen wanneer ze hun pauze nemen.                                                                       | Test 3.1  | 24/02/2024 |
| DR31  | Het systeem mag geen extra werkdruk of cognitieve belasting veroorzaken.                                                                | Test 3.1  | 24/02/2024 |
| DR32  | Een snooze-functie moet mogelijk zijn om pauzes uit te stellen.                                                                         | Test 3.1  | 24/02/2024 |
| DR34  | Het systeem moet rekening houden met piekmomenten (ochtend- en avondzorgen) bij pauzevoorstellen.                                      | Test 3.1  | 24/02/2024 |
| DR40   | Iedereens manier van signaalgeven moet gekozen kunnen worden.                                                                                                                 | Test 3.2 | 6/03/2025  |
| DR42   | Voor het hele ‘ecosysteem’ ontwerpen, niet enkel zorgmedewerkers.                                                                                                             | Test 3.2 | 6/03/2025  |
| DR45  | Het mag geen grote veranderingen (“Franse Revolutie”) veroorzaken, maar het moet wel waardevol zijn.                                                                          | Test 3.2 | 6/03/2025  |
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

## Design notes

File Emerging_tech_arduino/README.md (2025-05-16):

# Emerging_tech_arduino
De overkoepelende opdracht voor het vak Opkomende Technologieën beschrijft het realiseren van een Wizard of Oz prototype voor het project van het vak project gebruiksgericht ontwerpen. Het project kan als volgt in een notendop worden beschreven: een wearable die het stressniveau van een zorgverlener communiceert naar een feedbackunit die dit stressniveau van zorgverleners visualiseert met een bewegend dier als metafoor. Het doel hiervan is om meer aandacht te bieden aan stress binnen zorginstellingen, zodat hier beter op ingespeeld kan worden en burn-outs en uitval door stress op lange termijn kunnen worden voorkomen.

Aangezien de hoofdzakelijke focus voornamelijk op de feedbackunit ligt, zal enkel dit aspect worden uitgewerkt als prototype. Als metafoor is gekozen voor een hond die verschillende houdingen kan aannemen: van staand naar zittend en alle tussenliggende posities. De positie van de hond geeft het stressniveau van de zorgverlener weer.
Bijkomend is het de bedoeling dat de feedbackunit enkel de stress status aangeeft als de betreffende gebruiker in de buurt is, dit om negatieve stigmatisering te beperken.
Concreet moet dit prototype voldoen aan volgende vereisten om het te kunnen beschouwen als een geslaagd wizard of zo prototype:

| Vereiste                                                        | Methode/Technologie             |
|------------------------------------------------------------------|----------------------------------|
| Hond die van staan naar zitten beweegt, inclusief tussenposities | Servomotor                       |
| Visuele aanduiding van stressniveau                              | Adafruit Neopixel 12 LED-ring    |
| Draadloze bediening (aan/uit, houdingen, nauwkeurige positiebepaling) | IR-afstandsbediening en -ontvanger |

## Elektronica
Gebruikte componenten:
- [12 led's ledring](https://www.otronic.nl/nl/12-bit-rgb-leds-ws2812b-cirkel-rond-neop-140567797.html?source=googlebase&gad_campaignid=19639985996
)
- [330 ohm weerstand](https://www.bitsandparts.nl/Weerstand-330-Ohm-1-4W-5pct-p101277?gQT=1)
- [Micro servomotor](https://www.bitsandparts.nl/Servo-motor-analoog-Micro-Servo-9g-SG90-180%C2%B0-p1907205?gQT=1)
- [IR-sensor](https://www.amazon.com.be/-/nl/LAOMAO-IR-zender-ontvanger-infrarood-diode/dp/B00EFOTJZE/ref=asc_df_B00EFOTJZE?mcid=ccc62f0bed2f3b54b88e6d84a187dd9d&hvadid=714474122054&hvpos=&hvnetw=g&hvrand=13440445988076704702&hvpone=&hvptwo=&hvqmt=&hvdev=c&hvdvcmdl=&hvlocint=&hvlocphy=9197127&hvtargid=pla-391957536169&psc=1&language=nl_BE)
- [9V batterij](https://www.amazon.com.be/-/nl/Duracell-Plus-Power-Alkaline-batterijen-stuks/dp/B00L6ZBJQC/ref=asc_df_B00L6ZBJQC?mcid=0bd8d411819c35bea0549e8427ceeeae&hvadid=714355656954&hvpos=&hvnetw=g&hvrand=1374928461625661830&hvpone=&hvptwo=&hvqmt=&hvdev=c&hvdvcmdl=&hvlocint=&hvlocphy=9197127&hvtargid=pla-423435131457&psc=1&language=nl_BE)
- [Arduino UNO](https://www.bitsandparts.nl/product/FUNDUINO_ARDUINO_UNO_R3?gad_campaignid=22404178302)
- [Breadboard](https://sinuss.be/products/psg-bb-170w-breadboard-170-pin-white-pro-signal?currency=EUR)

## Bedradingsschema
Dit schema toont een Arduino Uno die wordt aangestuurd via een IR-afstandsbediening. De IR-ontvanger ontvangt signalen en stuurt die naar de Arduino. Hiermee worden een NeoPixel LED-ring en een servomotor aangestuurd. De LED-ring is verbonden via een 330 ohm weerstand en krijgt, net als de servo, stroom via het breadboard.
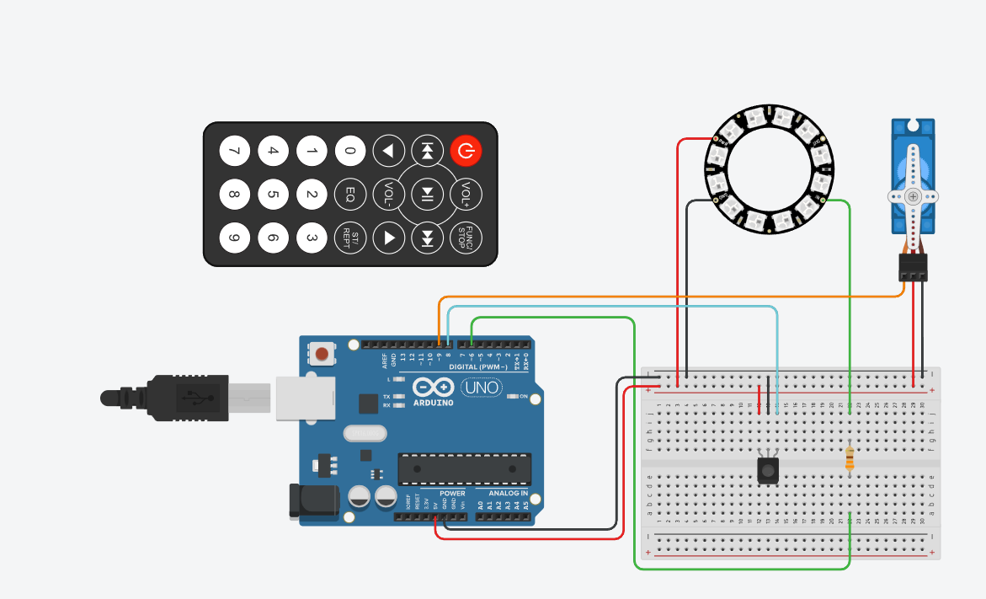
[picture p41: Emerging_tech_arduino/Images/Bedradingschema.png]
 

## Workflow
Om het project gestructureerd aan te pakken, werd het opgedeeld in twee delen: de basiswerking en mogelijke uitbreidingen. Dit zorgt ervoor dat eerst de essentiële functies volledig en stabiel werken, zodat er op een betrouwbare manier verder kan worden gebouwd. Een werkend prototype vereist in elk geval een correct functionerende basis.

**Basiswerking**

De basisfunctionaliteit bestaat uit het laten bewegen van een 3D-print van een hond (via een servomotor) en het weergeven van een LED-signaal (via een ledring). Deze twee elementen reageren op input via een IR-afstandsbediening.
De stappen die hiervoor werden gevolgd:
1.	IR-signalen uitlezen via de seriële monitor.
2.	Verschillende binnenkomende IR-codes herkennen en onderscheiden.
3.	De servomotor aansturen op basis van een geselecteerd IR-commando.
4.	De LED-ring tegelijk met de servo laten reageren op dezelfde input.
   
**Uitbreiding**

In een latere fase kan het systeem uitgebreid worden met een proximityfunctie via Bluetooth. Hierbij werkt de feedbackunit (servo + LED) pas als de gebruiker, die een wearable draagt, zich binnen een bepaalde afstand bevindt.
De uitbreidingsstappen:
1.	Een toestel ontwikkelen dat een Bluetoothsignaal uitzendt (simulatie van de wearable).
2.	De nabijheid van dit toestel meten aan de hand van de signaalsterkte (RSSI).
   
**Aanpak**

Als eerste werd een verbinding gelegd tussen de Arduino en de IR-ontvanger. Met behulp van de seriële monitor konden de unieke codes van elke knop op de afstandsbediening gelogd worden. Vervolgens werd de servomotor aangestuurd op basis van een gekozen IR-waarde. Toen dit betrouwbaar werkte, werd de LED-ring apart getest en later toegevoegd aan de code. Pas toen alle onderdelen afzonderlijk goed functioneerden, werden ze geïntegreerd in één programma. Hieronder is een flowchart gevisualiseerd van de aanpak voor de basiswerking en ook een video van het eerste resultaat.

<div align="center">
  <table>
    <tr>
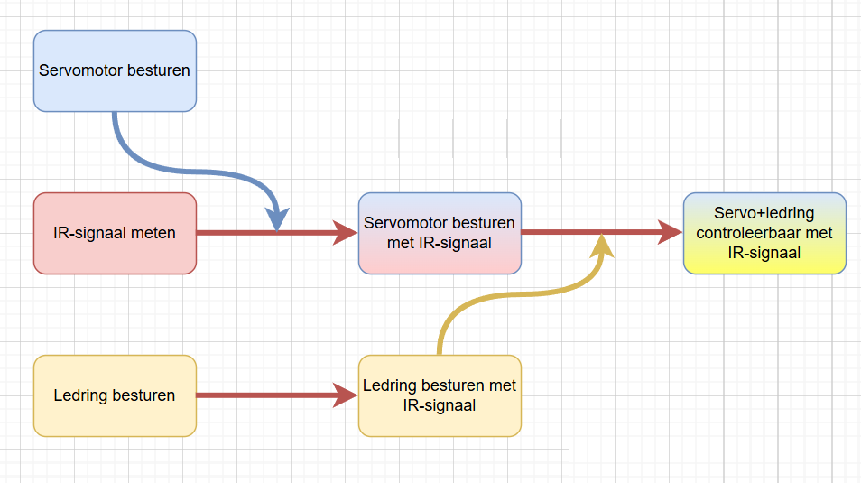
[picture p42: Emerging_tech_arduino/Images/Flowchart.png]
Flowchart
      <td></td>
      <td>Demo</td>
    </tr>
  </table>
</div>

## Problemen onderweg
Zoals bij elk ontwikkelingsproces verliep ook dit project niet zonder uitdagingen. In dit onderdeel worden de belangrijkste problemen besproken die zich tijdens het ontwikkelen van het prototype hebben voorgedaan, samen met de oplossingen die werden toegepast. Elk probleem droeg bij aan een beter begrip van de beperkingen van zowel hardware als software.

### Beperkte functionaliteit in vroege versie
In de eerste versies kon de hond enkel naar een andere positie bewegen (bijvoorbeeld van zittend naar staand) door herhaaldelijk op de plus- of minknop van de afstandsbediening te drukken. Dit was niet alleen onhandig, maar ook weinig representatief voor een realistische interactie. Daarom werd de code uitgebreid zodat specifieke knoppen een voorgeprogrammeerde doelpositie activeren, zoals “zit”, “neutraal” of “sta”. Daarnaast werd er ook een aan-uitknop gedefinieerd. Hierdoor werd de besturing intuïtiever en gebruiksvriendelijker.

### Bounce op bedieningsknoppen
Tijdens de eerste testen bleek dat één druk op een knop van de afstandsbediening vaak als meerdere drukken werd geïnterpreteerd. Dit zorgde ervoor dat bijvoorbeeld het systeem ongewild meerdere keren aan en uit werd geschakeld of de servo te ver bewoog.
Het probleem kwam voort uit het ontbreken van debounce-logica: IR-signalen worden zeer snel na elkaar herhaald verzonden, waardoor één druk meerdere commando’s genereert.
De oplossing was om een softwarematige debounce te implementeren, waarbij voor elke knop (met name de aan/uit-knop) een minimale wachttijd (bijvoorbeeld 500 ms) tussen opeenvolgende acties werd ingevoerd. Dit zorgt voor betrouwbaardere en stabielere bediening van het systeem.

### Servo beweegt ongewild
Aanvankelijk maakte de servo regelmatig kleine, ongewenste bewegingen, zelfs zonder geldige IR-commando’s. Dit leidde tot veel frustratie, aangezien het leek alsof de motor uit zichzelf begon te bewegen. Na uitgebreide debugging bleek dit te komen doordat de IR-ontvanger voortdurend irrelevante signalen registreerde (zoals code 0 en 64), die elke keer opnieuw verwerkt werden. Hierdoor werd telkens een minisignaal naar de servo gestuurd, wat kleine verschuivingen veroorzaakte.
De oplossing bestond erin om de servo alleen nog aan te sturen wanneer er een geldig commando wordt ontvangen (enkel codes 7, 12, 21, 24 of 94). In alle andere gevallen blijft de servo inactief. 

### Interferentie in bekabeling
Op een bepaald moment bleef de servo bewegen op een onverwachte manier, ondanks dat alle software correct leek. Het bleek dat de voedingskabel en de signaalkabel van de servo te dicht bij elkaar lagen, wat elektrische interferentie veroorzaakte.
Door de voedingskabels van de servo te koppelen met een 2de arduino, werd het probleem opgelost. De opstelling na het oplossen van dit probleem zag er als volgt uit:

<p align="center">
  
  
</p>

Uiteraard was deze opstelling niet optimaal, zeker aangezien de beschikbare inbouwruimte beperkt was. Om deze reden is er na veel zoeken een relatief eenvoudige oplossing bedacht die het mogelijk maakt om de schakeling te doen werken met slechtst 1 arduino die voorzien wordt van voeding door een 9V batterij. De oplossing was om de servo automatisch los te koppelen (detach) wanneer deze niet actief beweegt, waardoor de schokkende minibewegingen geen effect meer hadden op de servo.

### Servo beweegt bij opstart
Bij het inschakelen van de Arduino bleek de servo zich spontaan naar een standaardpositie te verplaatsen. Dit was ongewenst omdat dit kan zorgen voor schade, zeker wanneer de hond fysiek al in een andere positie stond.
De oplossing hiervoor was om bij het opstarten van de Arduino de huidige servo-positie uit te lezen en als beginpositie te registreren. Hierdoor worden onnodige bewegingen bij het opstarten vermeden.

### Delay blokkeert IR-signalen
In het oorspronkelijke programma werd een delay(18) gebruikt om de LED-ring te laten pulseren. Dit zorgde er echter voor dat inkomende IR-signalen niet altijd tijdig geregistreerd werden.
De oplossing was om delay() te vervangen door een millis()-gebaseerde aanpak, waarmee gecontroleerd wordt of er voldoende tijd is verstreken sinds de vorige LED-update. Hierdoor blijft het systeem responsief voor afstandsbedieningscommando’s.

### Onbetrouwbare interrupt-afhandeling
Er werd geëxperimenteerd met interrupts om de IR-signalen te detecteren. In theorie zou dit sneller en efficiënter werken. In praktijk bleek echter dat ongewenste of ‘ruis’-signalen vaak foute triggers veroorzaakten, waardoor valse commando’s werden geregistreerd.
Uiteindelijk werd gekozen om interrupts volledig te vermijden en over te schakelen op polling via de IrRemote-bibliotheek. Deze bleek veel stabieler en nauwkeuriger in het correct verwerken van inkomende IR-commando’s.

### Beperkingen van Tinkercad
Tinkercad bleek niet compatibel met de Adafruit NeoPixel-bibliotheek, wat betekent dat de LED-functionaliteit niet virtueel getest kon worden. Daardoor moest de volledige schakeling meteen in de echte wereld opgebouwd en getest worden.

## Code
De werkende Arduino scripts zijn te vinden via: [code/arduino](Codes/CombinatieServoLedRingV3)

### **Opstart**
In het eerste deel van de code worden libraries en variabelen gedeclareerd om de Arduino te bedienen met een servo-motor, een NeoPixel LED-ring en een IR-afstandsbediening. Daarnaast staat er uitleg over de aansluiting van het prototype en welke libraries geïnstalleerd moeten worden.

```yaml annotate
//Bram Finn Pieter

/*
Aansluitingen:
ledStrip: GND (Grijze kabel) -> GND arduino, 5V (Witte kabel) -> 5V arduino, D (Paarse kabel) -> pin 6
Servo: GND (zwarte kabel) -> GND arduino, 5V (rode kabel) -> 5V arduino, Signaal (Oranje kabel) -> pin 9
IRsensor: GND met GND, 5V met 5V, Output (linker pootje)-> pin 8

Installeer de libraries:
"Adafruit_NeoPixel.h", 
"IRremote" by shirriff, z3to, ArminJo
"Servo" by Micheal Margolis, Arduino

Met behulp van een IR-bakje kan je het besturen.
De servo kan aangestuurd worden met het bakje.
De kleur van de ledring hangt af va nde hoek van de servo.
*/
#include <IRremote.hpp>
#include <Servo.h>
#include <Adafruit_NeoPixel.h>

#define IR_RECEIVE_PIN 8
#define SERVO_PIN 9
#define LED_PIN 6
#define LED_COUNT 12

Adafruit_NeoPixel strip(LED_COUNT, LED_PIN, NEO_GRB + NEO_KHZ800);
Servo servo;

int pos = 0;
int targetPos = 0;
bool systeemActief = true;
bool positieVeranderd = false;
bool servoIsAttached = false;

int RoodGB= 0;
int RGroenB= 0;
int RGblauw=0;
int stapRichting=1;

uint32_t Kleur_Ledring = strip.Color(0, 0, 0);    
unsigned long vorigeTijd = 0;
unsigned long tijd=0;
unsigned long tijdsVerschil=0;

// Debounce
unsigned long laatsteToggleTijd = 0;
const unsigned long debounceInterval = 500;
```

### **Void setup**
In de void setup van de code initialisesert de seriële communicatie, de IR-ontvanger, de LED-strip en de servo, en stelt de beginpositie van de servo in. Het geeft deze startpositie dan ook weer op de seriële monitor.
```yaml annotate
void setup() {
  Serial.begin(9600);
  IrReceiver.begin(IR_RECEIVE_PIN);
  strip.begin();
  strip.show();  // zet alle leds uit

  delay(500);             // tijd om servo manueel te plaatsen
  pos = targetPos = servo.read(); // positie bewaren bij opstart
  Serial.print("Startpositie: ");
  Serial.println(pos);
}
```
### **Besturing ledring**
In deze aparte void-functie wordt de LED-ring aangestuurd. Dit is zo opgezet zodat de functie eenvoudig te hergebruiken en te integreren is in andere codes.
```yaml annotate
void besturingLedring(int aantalLeds, uint32_t kleur) {
  for (int i = 0; i < LED_COUNT; i++) {
      strip.setPixelColor(i, kleur);
    } 
  strip.show();
  }
```

### **Void loop**
Alle code die hieronder staat, bevindt zich binnen de void loop.

#### **IR-signaal**
De code ontvangt IR-commando's om het systeem aan of uit te zetten, de servo te bewegen en de LED-strip te bedienen. Daarbij voorkomt een debounce dat commando's te snel achter elkaar worden verwerkt. Tegelijkertijd wordt de doelhoek voor de servo ingesteld.
```yaml annotate
  if (IrReceiver.decode()) {
    int cmd = IrReceiver.decodedIRData.command;
    Serial.print("Ontvangen IR commando: ");
    Serial.println(cmd);

    if (cmd == 22 && (millis() - laatsteToggleTijd > debounceInterval)) {
      systeemActief = !systeemActief;
      laatsteToggleTijd = millis();

      Serial.print("Systeem actief: ");
      Serial.println(systeemActief ? "JA" : "NEE");

      if (!systeemActief) {
        if (servoIsAttached) {
          servo.detach();
          servoIsAttached = false;
          Serial.println("Servo losgekoppeld (systeem uit)");
        }
        strip.clear();
        strip.show();
      }
    }

    IrReceiver.resume();
  }

    if (systeemActief) {
      if (cmd == 7)    { targetPos = constrain(pos + 10, 110, 190); positieVeranderd = true; }
      if (cmd == 21)   { targetPos = constrain(pos - 10, 110, 190); positieVeranderd = true; }
      if (cmd == 12)   { targetPos = 110; positieVeranderd = true; }
      if (cmd == 24)   { targetPos = 150; positieVeranderd = true; }
      if (cmd == 94)   { targetPos = 190; positieVeranderd = true; }

      // Servo pas opnieuw koppelen bij nieuwe beweging
      if (positieVeranderd && !servoIsAttached) {
        servo.attach(SERVO_PIN);
        servoIsAttached = true;
        Serial.println("Servo opnieuw gekoppeld");
      }
    }

    IrReceiver.resume();
```

#### **Servo**
Hieronder staat de code die de servo langzaam beweegt naar de doelpositie wanneer het systeem actief is en de positie is veranderd.
```yaml annotate
  if (systeemActief && positieVeranderd && servoIsAttached) {
    if (pos != targetPos) {
      pos += (pos < targetPos) ? 1 : -1;
      servo.write(pos);
      delay(20);
    } else {
      positieVeranderd = false;

      // Servo uitschakelen als beweging klaar is
      servo.detach();
      servoIsAttached = false;
      Serial.println("Servo beweging voltooid → detach()");
    }
  }
```

### **Ledring**
Dit deel zorgt ervoor dat de LED-ring pulserend werkt zolang het systeem actief is. De kleur verandert afhankelijk van de hoek die de servo moet aannemen.
```yaml annotate
  // LED pulsering
  if (systeemActief) {
      tijd=millis();// werken met Millis voor delay te vervangen -> focus op 16 keer pulseren per minuut (ademhalingsritme) -
      tijdsVerschil= round(tijd-vorigeTijd);
      if (tijdsVerschil >= 18.75) {
        vorigeTijd = tijd;
      }

      // Rustig groen pulserend 
      // Groen 50 naar 255
      if (targetPos == 190 && tijdsVerschil>18.75) {
        if (RoodGB>=254) {stapRichting = -1;}
        else if (RoodGB<=80) {stapRichting = 1;}
        RoodGB = RoodGB + stapRichting * 1.75;
        RGroenB = 10+ (RoodGB-80)/3.5;// RGroenB is afhankelijk van RoodGB
        RoodGB = constrain(RoodGB, 80, 255);
        RGroenB = constrain(RGroenB, 10, 60);

        Kleur_Ledring = strip.Color(RoodGB, RGroenB, 0);
        besturingLedring(12, Kleur_Ledring);
      }
            // Rustig groen pulserend 
      // Groen 50 naar 200
      else if (tijdsVerschil>18.75){// 18.75 -> 16 keer pulseren per minuut (ademhalingstempo)
        if (RGroenB>=200) {stapRichting =-1;} // eenmaal het maximaal heeft bereikt 
        else if (RGroenB<=50) {stapRichting =1;}
        RGroenB = RGroenB + stapRichting * (200-50)/100; // 2.05= (200-50)/100
        RGroenB = constrain(RGroenB, 50, 200); // extra veiligheid

        Kleur_Ledring = strip.Color(0, RGroenB, 0); // RGB-code toekennen aan een variable
        besturingLedring(12, Kleur_Ledring); // variable doorsturen naar zelfgemaakte functie die ledRing aanstuurt (zie onder void loop)
      }
    }
```

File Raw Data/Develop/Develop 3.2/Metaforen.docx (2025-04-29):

Nr. | Afbeelding | Concept | Bevinden

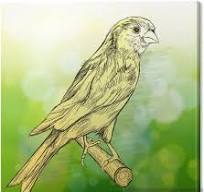
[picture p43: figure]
Canvas Schets van een kanarie vogel zit op een tak

| | Vogel vliegt tijdens goed bevinden. Landt op tak wanneer er pauze moet worden genomen. | Joy, “herkenbaar”

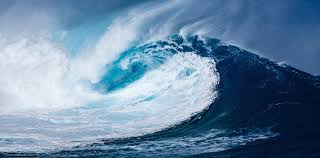
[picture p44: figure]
Waarom je van het kijken naar golven gelukkig wordt

2 | | Golf beweging met lichtsignaal cfr. Wii disk input

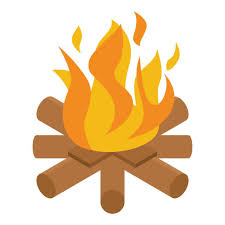
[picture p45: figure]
kampvuur icoon, isometrische stijl 15201261 Vectorkunst bij Vecteezy

3 | | Kampvuur dat begint te smeulen bij verminderde prestatie en harder brandt naarmate “performantie” | Grieve (kampvuur begint de verminderen) “te pusherig, slecht zelfbeeld”

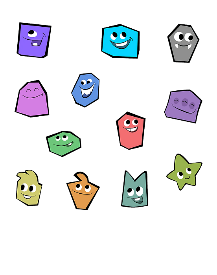
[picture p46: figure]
Jackbox Party Quiplash Unisex For Men Women Dmn Hoodie Black I Love This Tapestry

4 | | Companion die zoals staafje omhoog komt.

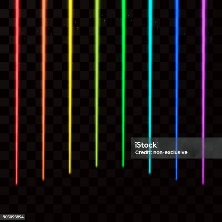
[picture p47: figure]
Neon Glowing Sticks Laser Beams With Light Thunder Bolt Effect Iridescent Rainbow Colors Cyber Energy Tubes Flying Sparkles And Flash Explosion Magic Wand Or Rod Vector Illustration-vektorgrafik och fler bilder på Blixt -

5 | | Lichtgevende balkjes die kunnen pulseren | “onduidelijk, amazement”

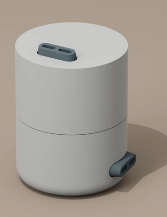
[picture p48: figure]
Afbeelding met cilinder, overdekt, ontwerp Door AI gegenereerde inhoud is mogelijk onjuist.

6 | | Ventilator die gaat draaien en lucht blaast

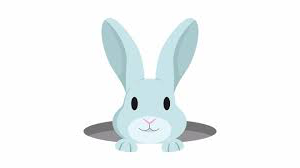
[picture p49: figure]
Rabbit Peeps Out Of Hole On Alpha - Stock Motion Graphics | Motion Array

7 | | Konijn dat komt kijken uit gat | Joy,

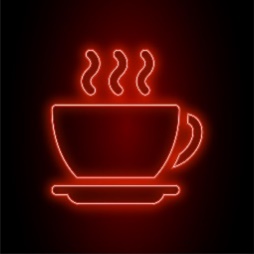
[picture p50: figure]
Premium Vector | High Impact Red Neon Coffee Cup Icon with Dark Background

8 | | Koffietas die gaat oplichten: opvullen naar mate nodig is: vol → pauze | Tof ideetje (als je tas beneden vol is heb je weinig stress, “koffietas vind ik ne leuke, heel duidelijk”

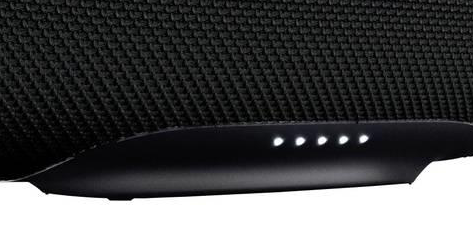
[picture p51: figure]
JBL Charge 4 – Canoon Store

9 | | Oplaadanimatie jbl
10 | | Lamp die begint te branden/pulseren

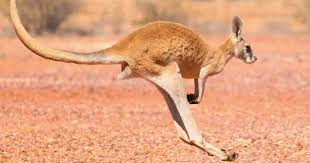
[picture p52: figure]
Kangaroos | Bush Heritage Australia

11 | | Kangoeroe die springt om te stimuleren. Die gaat zitten om te kalmeren | Tof maar hoe is het mogelijk “die kangoeroe vind ik wel tof”

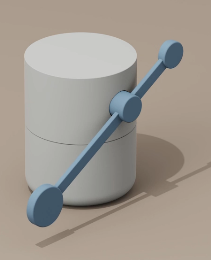
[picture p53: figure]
Afbeelding met cilinder, Huisraad, overdekt Door AI gegenereerde inhoud is mogelijk onjuist.

12 | | Constant bewegend object dat plots hard gaat bewegen/stilstaat | “luchtkwaliteit corona referentie: met kanariepeitje” Absoluut niet met geluid, het zou me stress geven , “goed snel, stress traag”

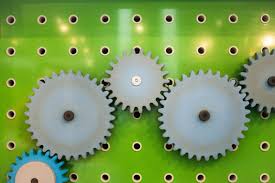
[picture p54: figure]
Experiment: Draaien alle tandwielen even snel rond? - Technopolis

13 | | Tandwielen die blijven draaien/ vaststuiken/ stoppen | Anger, “blijft maar draaien, je blijft maar bezig”

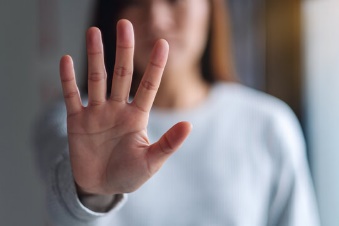
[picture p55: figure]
Stop Sign Hand Images – Browse 303,869 Stock Photos, Vectors, and Video | Adobe Stock

14 | | Hand die omhoog gaat/ gebaar uitdrukt. | Dit is wel een goeien, duidelijk signaal. Anger

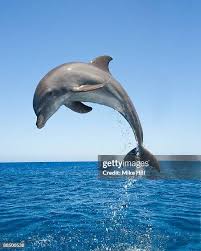
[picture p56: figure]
563 Dolphin Jumping Stock Photos, High-Res Pictures, and Images - Getty Images

15 | | Dolfijn die uit het water springt | Ontspanningen (1) (2) content (3) (4): “dolfijn is blij”

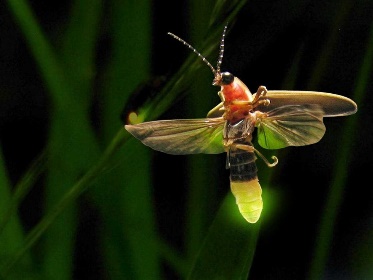
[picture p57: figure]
Vuurvliegje of lucciola in noord-Italie - Riorequesa.com

16 | | Vuurvliegje dat begint te pulseren/bewegen

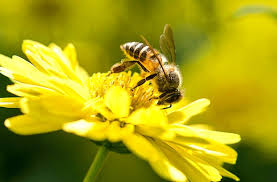
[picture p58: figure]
26,378 Bee Eating Nectar Royalty-Free Images, Stock Photos & Pictures | Shutterstock

17 | | Bloem met bij op die sluit om de bij bij stress

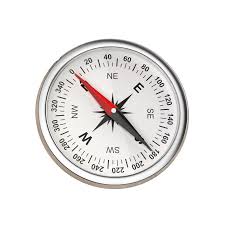
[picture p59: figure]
Plotting Compass | Magnetic Accessories | Magnets 4 U

18 | | Kompas dat begint te draaien | “draaien geeft angst, ik ben de weg kwijt”

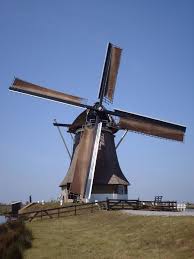
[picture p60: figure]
Windmolens in Nederland - Wikipedia

19 | | Windmolen die draait | (2) ontspannen “omgekeerde draaibeweging”

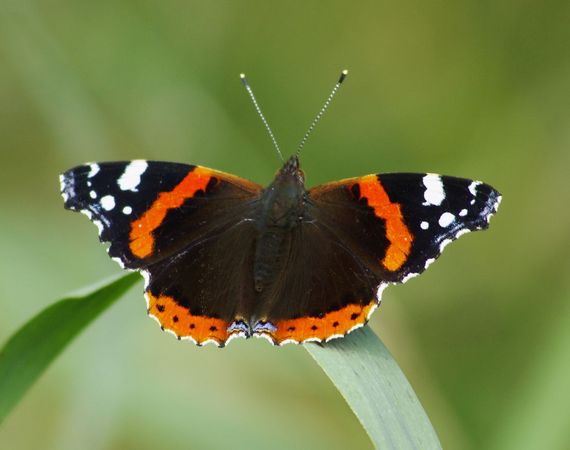
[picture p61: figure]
De Vlinderstichting | Trekvlinders

20 | | Vlinder die werkt zoals vogel en rust op bloem | “metafoor voor utopie: vlinder”(2) (4): rustgevend

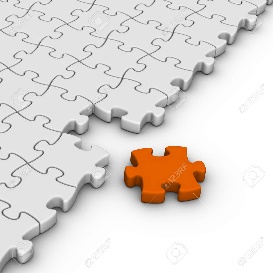
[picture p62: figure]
Gray Jigsaw Puzzles With One Orange Piece Stock Photo, Picture and Royalty Free Image. Image 12374318.

21 | | Puzzelstukken die oplichten en naar boven komen.

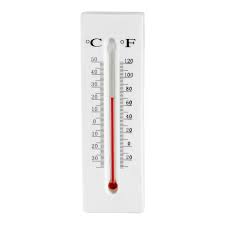
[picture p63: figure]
Thermometer “Sleutelverstopplaats”

22 | | Thermometer die stijgt | “(3) hoe meer gestresst hoe kwader je bent”

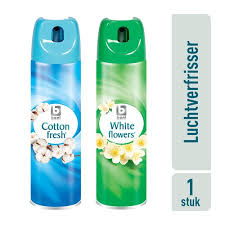
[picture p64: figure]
BONI luchtverfrisser assortiment 240ml | Colruyt - Collect&Go

23 | | Luchtverfrisser die geur verspreid o.b.v. stress? | “komt als verwarrend over: surprise”

A bright sun behind clouds at sunset. 47602087 Stock Photo at Vecteezy

24 | | Een zon die vanachter de wolken verschijnt | “geeft een goed en war gevoel”

Gratis afbeelding: eenden, verbergen, gras, moeras, lake, riet, watervogels, vogels, moeras

25 | | Een eend die uit het riet verschijnt

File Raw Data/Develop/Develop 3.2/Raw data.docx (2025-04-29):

# Raw data

Algemene: met dieren als metaforen werken is persoonlijk en vaak zeer welkom

1&2

"da gaat bij mij bijvoorbeeld niet direct werken"--> dummy mode

ook ergotherapeuten? verschillende perspectieven verzamelen--> heel werk-ecosysteem verkennen

"er wordt ook telkens meer verwacht, voor mij is dat een grote stressfactor"

"een pil geven is een pil aftekenen"

“Focus houden en uw werk een stuk aanhouden” “Gewoon dus harder werken” (1. Zeer sterk ontevreden bij uitspraak harder werken, 2. “comes as it goes” inwendig wel managen door bijv pauze later te nemen.

“het weer, voldoende personeel”, “snoezelbad, wandeling buiten → kleine zaken vooral sterk empatisch: feel good bij bewoner aanbrengen”

“je moet leren loslaten: vandaag is het druk, morgen beter”

“onderlinge ventilatie: tegen elkaar “klagen””

“PC- wordt aan de kant gehouden en de mensen eerst → bureauwerk aan de kant en kan wachten”

“uitleg feedback unit: open voor idee en nieuwsgierig”

wat zou je toevoegen Het weer: de zon

"tijdens de late dienst is er geen zorgkar"

"vaste punten?: niet direct te thuisbrengen, ik moet zeggen wij werken eigenlijk in stukken van 4 6 of 8 uur" afhankelijk van werktijd.

"Ik heb meer stress tijdens de late dienst dan de ochtenddienst

"Ik ben een ochtendmens"

3 & 4 (Bruno en Fien)

3 staat zeer open voor het concept, 4 stelt zich er nog vragen bij

“geluksmomenten: 3: Net na de middag, rustig moment: tijd om met een bewoner om te gaan, dan heb ik zelf drie kwartier tijd om pauze te nemen”

“zoomer, trillen is vervelend maar goede reminder, groen lampje dat ze weten waar ik zit: mensen bellen, herhaalde meldingen zijn vervelend, massagefunctie” “ de volgende staat gereed, we moeten voortdoen”

“godverd, staat weer beneden, als je stress ervaart moet het kalmeren: altijd een tegengestelde reactie oproepen: stress→ kalmeren”

“moet personaliseren: bijv lievelingsliedje dat afspeelt bij, drukken op knop “

“die kangoeroe vind ik wel tof”

“bureau, verpleegpost, komen er veel, maar wij niet”

“als ze niet weten van wie die kop koffie is, maakt het niet uit”

“weergave om snel te kunnen checken: om niet tot aan de FU te hoeven lopen”

“er zijn mensen die met de FU zouden weglopen”

“er zijn mensen die niet plezant zijn om te verzorgen omdat deze tegenstribbelen” → er zijn bewoners die gelinkt worden”

“onder mouw steken”

“gemiddelde van het team weergeven → extra balkje ervoor”

“eigen aan het profiel van een

“Pyschosociaal welzijn is een zwaard dat langs twee kanten snijdt: het wegblijven van interactie met bepaalde personen, geen aparte afdeling voor bewoners met dementie → vaak belastend voor collega’s → mag niet duidelijk zijn.”

“zeer waardevol dat het gemeten kan worden, geen franse revolutie starten “ we staan hier allemaal strak” er is geen oplossing.

Uitleg gieter

“Directeur is weigerachtig bij woord pauze, vindt het welzijn zeer goed”, vooral de waarom in het kader van psychosociaal welzijn bij het team aanbrengen.

Er moet beleidsmatig iets aan worden gedaan: er moet worden voor opengestaan

“zorgen voor begint bij goede zelfzorg”

“niet te visibel maken, moet op afstand zichtbaar zijn”

“Niet iedereen heeft baat bij het zien van andermans stressniveau → enkel gemiddelde”

“collega’s kennen elkaar ook, er was iemand waar het echt niet goed mee ging, het moet niet weggestoken worden maar enkel binnen de groep zichtbaar zijn”

“altijd welkom”

“ik zou de eerste zijn die het wilt testen” “chronos groep bijv.”

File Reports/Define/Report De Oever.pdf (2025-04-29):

Evaluatieformulier: Effectiviteit van Oefeningen op Stress (Formulier 1)

Datum: 19/12/24
Naam zorgverlener: Lise
Stressgevoelig: JA / NEE

Tijdstip Oefening

Zeer
| | Ineffectief
(1)
| | | Ineffectief
(2)

Beetje
| | | | Effectief
(3)
| | | | | Neutraal
(4)
| | | | | | Effectief
(5)

Zeer
| | | | | | | Effectief
(6)
| | | | | | | | Uitzonderlijk
| | | | | | | | Effectief (7)
7:30 | Opstart
| monitor
8:30 | Ademhaling | ☐ | ☐ | ☐ | ☐ | ☐ | ☐ | ☐
9:30 | Korte babbel | ☐ | ☐ | ☐ | ☐ | ☐ | ☐ | ☐
10:30 | Koffie/ een glas
water drinken ☐ | ☐ | ☐ | ☐ | ☐ | ☐ | ☐
11:30 | Buiten
| wandelen | ☐ | ☐ | ☐ | ☐ | ☐ | ☐ | ☐

12:30 Setup opladen

Evaluatieformulier: Effectiviteit van Oefeningen op Stress (Formulier 2) Datum: 23/12/24
Naam zorgverlener: Eudine
Stressgevoelig: JA / NEE

Tijdstip Oefening

Zeer
Ineffectief
(1)

Ineffectief
(2)

Beetje
Effectief
(3)

Neutraal
(4)

Effectief
(5)

Zeer
Effectief
(6)

Uitzonderlijk
Effectief (7)

7:30

Opstart
monitor

8:30

Koffie/ een glas
water drinken ☐ | ☐ | ☐ | ☐ | ☐ | ☐ | ☐

9:30

Buiten
wandelen | ☐ | ☐ | ☐ | ☐ | ☐ | ☐ | ☐
10:30 Ademhaling | ☐ | ☐ | ☐ | ☐ | ☐ | ☐ | ☐
11:30 Korte babbel | ☐ | ☐ | ☐ | ☐ | ☐ | ☐ | ☐

12:30 Setup opladen

Evaluatieformulier: Effectiviteit van Oefeningen op Stress (Formulier 3) Datum: 20/12/24
Naam zorgverlener: Veerle
Stressgevoelig: JA / NEE

Tijdstip Oefening

Zeer
Ineffectief
(1)

Ineffectief
(2)

Beetje
Effectief
(3)

Neutraal
(4)

Effectief
(5)

Zeer
Effectief
(6)

Uitzonderlijk
Effectief (7)

7:30

Opstart
monitor

8:30

Koffie/ een glas
water drinken ☐ | ☐ | ☐ | ☐ | ☐ | ☐ | ☐

9:30

Buiten
wandelen | ☐ | ☐ | ☐ | ☐ | ☐ | ☐ | ☐
10:30 Ademhaling | ☐ | ☐ | ☐ | ☐ | ☐ | ☐ | ☐
11:30 Korte babbel | ☐ | ☐ | ☐ | ☐ | ☐ | ☐ | ☐

12:30 Setup opladen

Evaluatieformulier: Effectiviteit van Oefeningen op Stress (Formulier 4) Datum: 17/12/24
Naam zorgverlener: Lore
Stressgevoelig: JA / NEE

Tijdstip Oefening

Zeer
Ineffectief
(1)

Ineffectief
(2)

Beetje
Effectief
(3)

Neutraal
(4)

Effectief
(5)

Zeer
Effectief
(6)

Uitzonderlijk
Effectief (7)

7:30

Opstart
monitor
8:30 | Ademhaling | ☐ | ☐ | ☐ | ☐ | ☐ | ☐ | ☐
9:30 | Korte babbel | ☐ | ☐ | ☐ | ☐ | ☐ | ☐ | ☐
10:30 | Koffie/ een glas
water drinken ☐ | ☐ | ☐ | ☐ | ☐ | ☐ | ☐

11:30 Buiten
| wandelen | ☐ | ☐ | ☐ | ☐ | ☐ | ☐ | ☐

12:30 Setup opladen

Evaluatieformulier: Effectiviteit van Oefeningen op Stress (Formulier 5) Datum: 18/12/24
Naam zorgverlener: Katrie
Stressgevoelig: JA / NEE

Tijdstip Oefening

Zeer
Ineffectief
(1)

Ineffectief
(2)

Beetje
Effectief
(3)

Neutraal
(4)

Effectief
(5)

Zeer
Effectief
(6)

Uitzonderlijk
Effectief (7)

7:30

Opstart
monitor
8:30 | Ademhaling | ☐ | ☐ | ☐ | ☐ | ☐ | ☐ | ☐
9:30 | Korte babbel | ☐ | ☐ | ☐ | ☐ | ☐ | ☐ | ☐
10:30 | Koffie/ een glas
water drinken ☐ | ☐ | ☐ | ☐ | ☐ | ☐ | ☐

11:30 Buiten
| wandelen | ☐ | ☐ | ☐ | ☐ | ☐ | ☐ | ☐

12:30 Setup opladen

# Samenvatting

Samenvatting evaluatieformulier:
De oefeningen helpen bij iedereen anders waardoor je geen specifieke oefening kan geven aan mensen. De oefeningen hebben geholpen met het kalmeren en helpt ze ook om erbij stil te staan.

Samenvatting hartslagdata:
Hierbij hebben we de hartslag gemeten over 10 minuten en dan kregen we de hoogste en laagste BPM terug. Hierbij merk je dat sommigen in de 100 zitten en anderen in de 70 maar de het verschil tussen de hoogste en laagste is wel een goede manier voor stress op te meten.

SAMENVATTING Vragen:
1 persoon/groep keek voor het onderhoudt van het prototype: kuisen + opladen. Het gebruik van dit product heeft geen effect op de bewoners.
Ze zouden het aan anderen aanraden.

Vorm:
Het mag iets kleiner, een zachter bandje, een handleiding voorzien (lag bij de hoofden(verantwoordelijken)). Er zat wel een kompres tussen zodat het bandje (velcro) niet zou snijden.
Het ging goed voor ermee te werken maar het moet wel robuust zijn omdat ze soms tegen iets zouden haperen. Het werd niet opgemerkt. (gevoel)
Voor 1 voormiddag was er geen probleem maar als het voor een hele week mag het iets comfortabeler.

Feedbackunit:
Soms merken het personeel het lichte niet omdat ze bezig waren, misschien iets van geluidje, trillingje,... gebruiken.

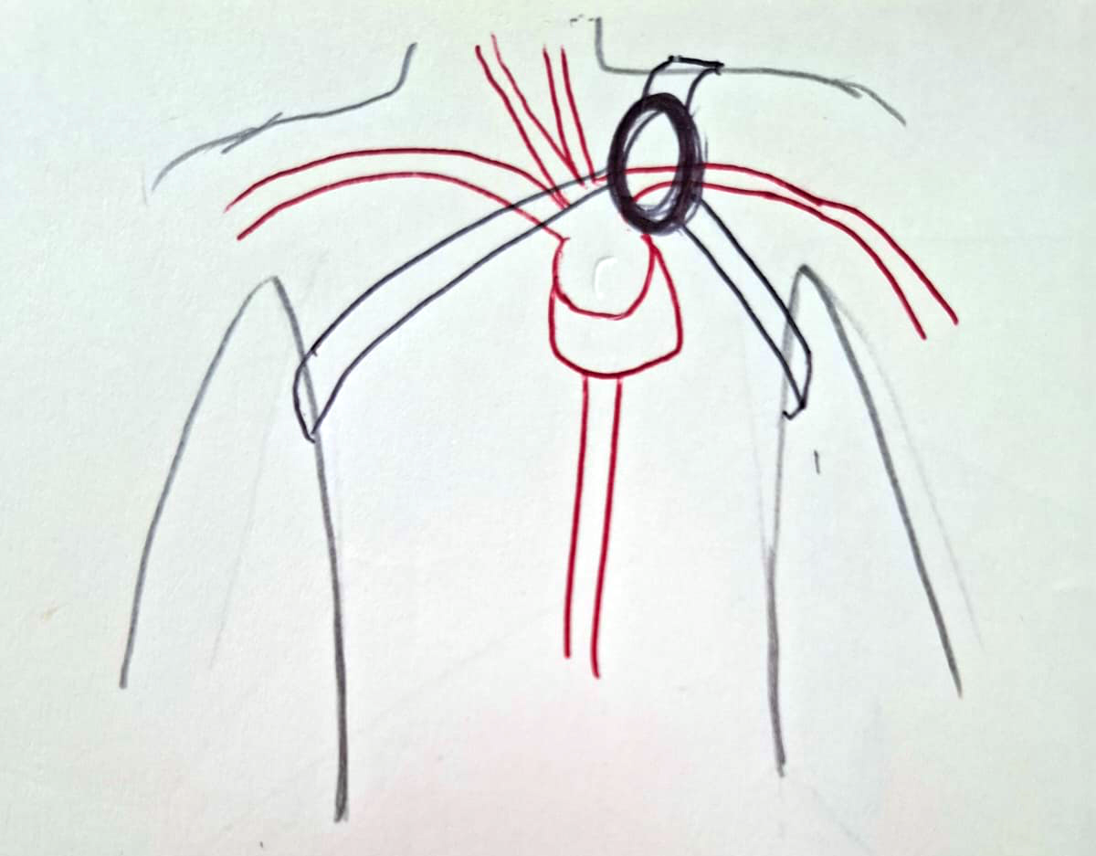
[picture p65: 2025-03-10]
Foto's/5 Definition/Wave 1/design wave 1.1.png

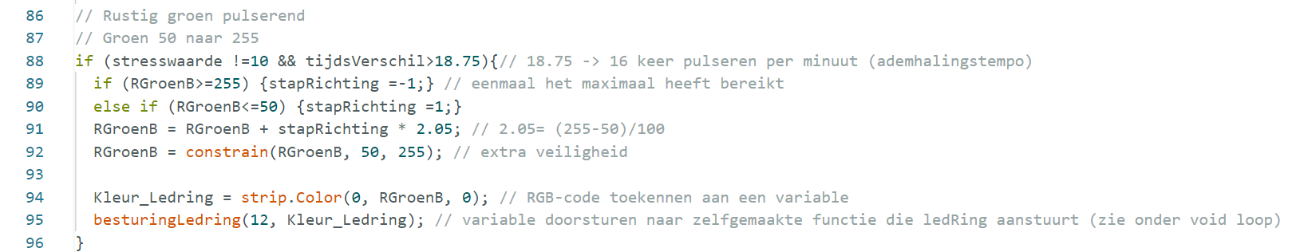
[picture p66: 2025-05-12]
Emerging_tech_arduino/Images/Images code/Pulseren van de ledring.png

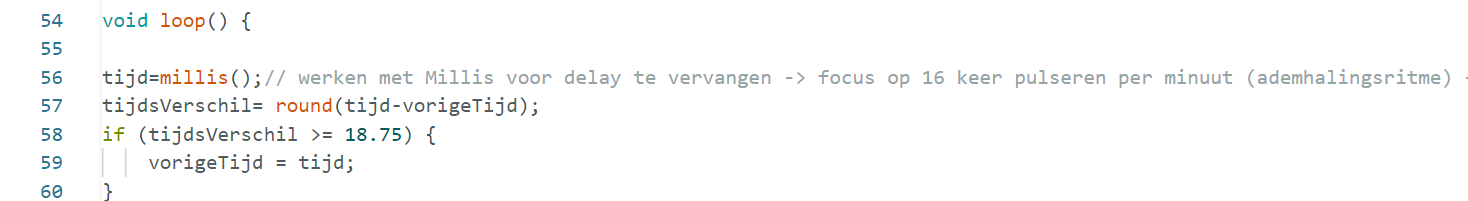
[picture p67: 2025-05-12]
Emerging_tech_arduino/Images/Images code/Start void loop, millis timer.png

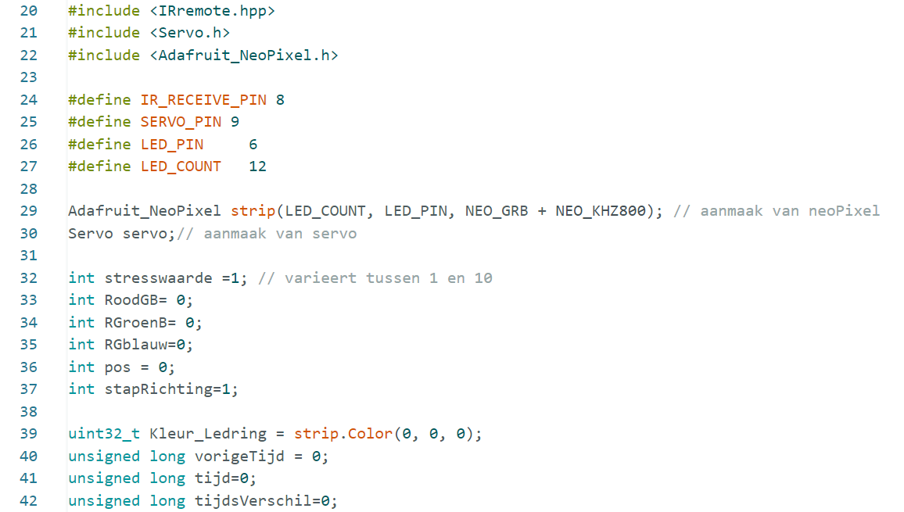
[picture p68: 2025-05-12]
Emerging_tech_arduino/Images/Images code/Lijntjes include, define.png

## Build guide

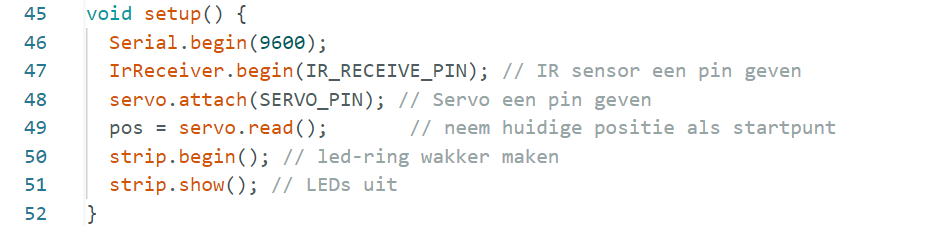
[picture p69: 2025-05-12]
Emerging_tech_arduino/Images/Images code/Void setup.png

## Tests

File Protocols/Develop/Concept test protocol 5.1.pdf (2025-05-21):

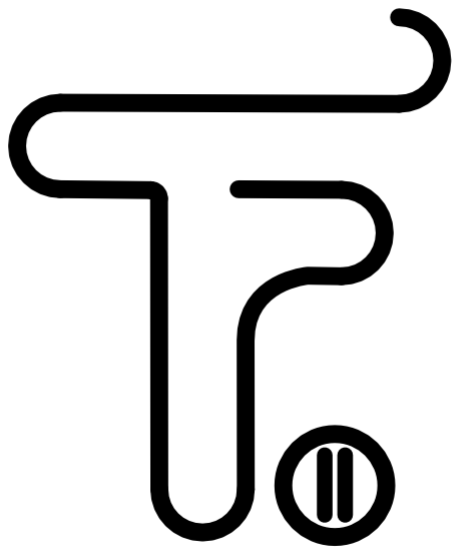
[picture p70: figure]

Vak: Gebruiksgericht ontwerpen Design Challenge: Werkbaar werk in de zorg Docenten: Bastiaan Baccarne & Yannick Christiaens Studenten: Demaegdt Pieter, Schrijvers Finn, Tops Bram

# Concept test protocol 5.1

# Inleiding

Dit concept test protocol wordt gekaderd binnen het vak gebruiksgericht ontwerpen met als thema: “Werkbaar werk in de zorg”. Take five heeft twee doelen, het analyseren, maar ook het bestrijden van burn-out bij zorgverleners die werken onder een hoge werkdruk. Dit gebeurd d.m.v. 3 componenten: een wearable die het stressniveau meet, een feedback unit die de status van alle gebruikers visualiseert en een verificator die doordachte pauzes zal voorstellen en loggen.

# Doel:

Op vlak van cognitieve ergonomie willen we het meest gebruikte voorwerp: de Feedback unit, zo esthetisch mogelijk laten passen binnen de gebruikte context: woonzorgcentra en ziekenhuizen. Dit alles gebeurt a.d.h.v. een enquête die het stramien van [1] volgt, dit is een studie rond het kwantitatief esthetisch meten van producten.
Het resultaat ervan zijn richtlijnen omtrent CMF, vorm en stijl; alsook het bevinden van mogelijke prototype-looks.
Analyse van deze inzichten en opgekomen ontwerpvragen zijn te vinden in Concept test rapport 5.1.docx (https://ugentbe-my.sharepoint.com/:w:/r/personal/bram_tops_ugent_be/Documents/2024-2025/Gebruiksgericht%20Ontwerpen/D5/Concept%20test%20rapport%205.1.docx?d=w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)

# Methode (n>30):

Doelgroep: Het interview wordt zo opgesteld dat iedereen dit kan invullen zonder enige voorkennis. Er wordt binnen verschillende leeftijdsgroepen getoetst door voornamelijk familie, kennissen en vrienden te toetsen.

Query effect: Om het query effect (de invloed van volgorde of te geringe verschillen tussen keuzemogelijkheden) te minimaliseren, worden de visuele inputvarianten per testtype voldoende contrasterend gekozen.
Voorbereidende opbouw interview:
Voorafgaand aan de test krijgen deelnemers een korte, gestandaardiseerde introductie over het doel van het onderzoek en de context van het product ("Take Five" feedbackunit). Hierbij wordt expliciet vermeld dat de test focust op esthetische en visuele perceptie, niet op technische functionaliteit.
Onderstaande vragen zijn gesteld met telkens:
- De input, die gepresenteerd wordt aan de gebruiker
- Hetgeen dat gemeten wordt
- Hoe men dit meet

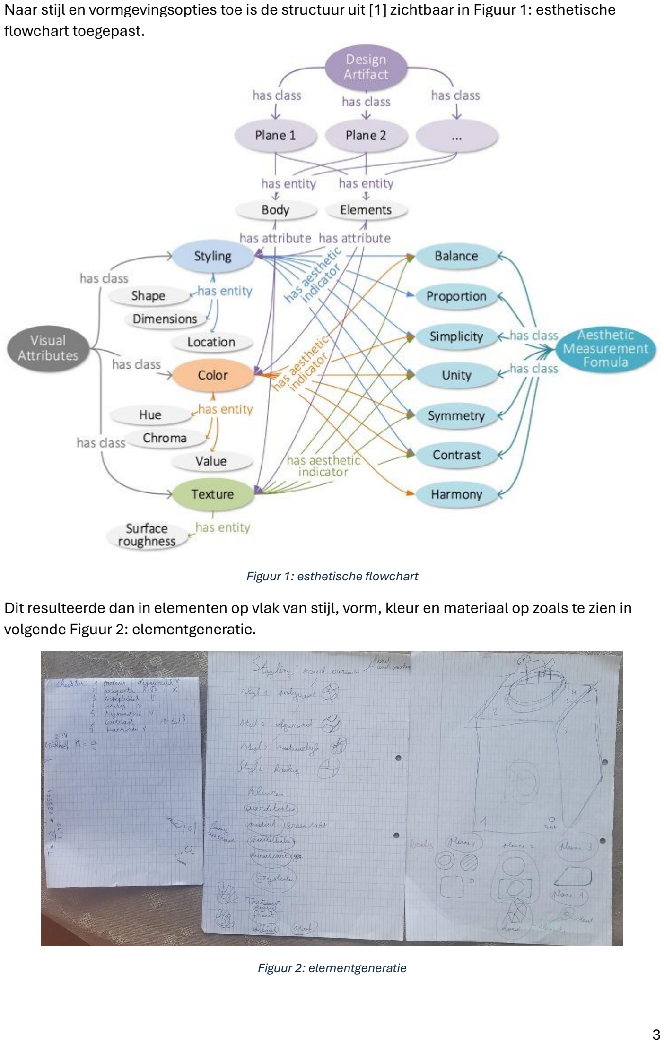
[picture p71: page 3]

Naar stijl en vormgevingsopties toe is de structuur uit [1] zichtbaar in Figuur 1: esthetische flowchart toegepast.

Figuur 1: esthetische flowchart
Dit resulteerde dan in elementen op vlak van stijl, vorm, kleur en materiaal op zoals te zien in volgende Figuur 2: elementgeneratie.

Figuur 2: elementgeneratie

## Materiaal:

- Online Survey via Qualtrics
- Digitale foto’s:
- Grijze “blanco” render van het stat-prototype
- 3 Moodboards
- 3Productrenders die stijl, vormgeving en CMF toepassen van de eerder getoonde moodboards
- 20 wordcards die met het product kunnen geassocieerd worden. O.b.v (eerdere interviews en [2])
- Prototypes:
- FU van Opkomende technologieën
- Video van de werking van het finale prototype: hond die een beweging uitvoert:
- Gaan zitten
- Rechtstaan

# Prototypes

Uit test rapport 4.1 (https://ugentbe-my.sharepoint.com/personal/bram_tops_ugent_be/Documents/2024-2025/Gebruiksgericht%20Ontwerpen/D4/Concept%20test%20rapport%204.1.docx?web=1) blijkt dat de gebruikte signalisatie bij een olifant niet als een intuïtief signaal wordt geïnterpreteerd. Daarom wordt er voor het huidige en laatste prototype gekozen voor een hond, de redenering hierachter kan gevonden worden in test rapport 3.2.
Op vlak van abstractie mag het metafoor herkenbaar zijn, maar toch abstract genoeg opdat dit niet als kinderachtig overkomt.
Verder liggen de fysieke beperkingen in werking en afmetingen bij de gebruikte elektronische componenten en grootte van het ge-3D-printte metafoor. Om dit alles uit te werken is er gemodelleerd o.b.v. de mechaniek van het prototype. En vervolgens een zo compact mogelijke behuizing ontworpen o.b.v. de afmetingen van de elektronica wat resulteert in onderstaande Figuur 3: vormgeving prototype.

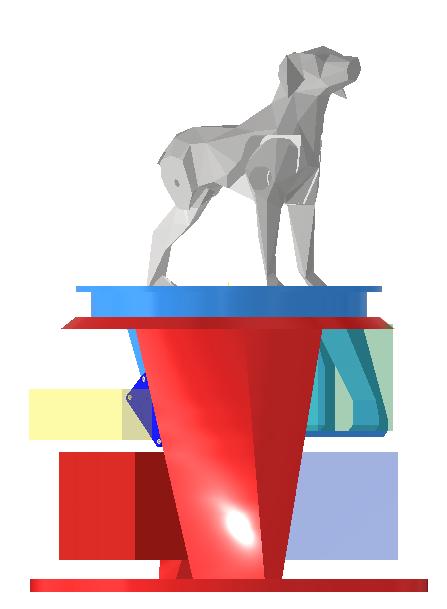
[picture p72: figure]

Figuur 3: vormgeving prototype
Vervolgens werden alle vroegtijdige tekortkomingen verfijnd en is men volgend finaal prototype bekomen, zichtbaar in Figuur 4: finaal prototype.

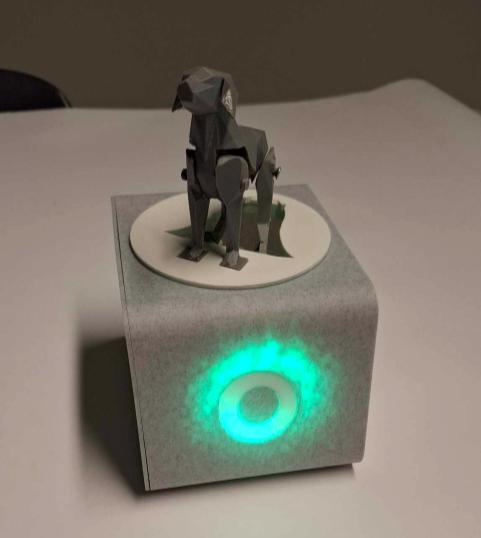
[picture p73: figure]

Figuur 4: finaal prototype

# Ontwerpvragen

De gestelde ontwerpvragen zijn de volgende:
- Welke esthetiek roept rust of vertrouwen op in een zorgcontext?
- Welke stijl sluit aan bij de mentale modellen van zorgverleners?
- Welke Vorm en afwerking straalt betrouwbaarheid uit?
- Welke gevoelens roept het ontwerp op?
- Wat is de initiële indruk van het ontwerp?
Het is hierbij belangrijk om gebruik te maken van eenduidige, concrete vragen die slechts één interpretatie toelaten.
Ook slechts een beperkt aantal opties per vraag aan te bieden. Eens dit in orde is dient de volgorde van de vragen logisch te verlopen.

# Respondenten

De enquête is getoetst bij: vrienden en familie alsook studenten. Door deze online te verspreiden, zijn enkel degene die de anonieme link hebben gebruikt familieleden. Verder zijn er enkele fysieke QR-codes gehangen on campus. De verdeling tussen volwassenen/grootouders en jongeren is weergegeven in Figuur 5: verdeling doelgroep.

Figuur 5: verdeling doelgroep

# Overzicht & structuur enquête

De enquête is beschikbaar via volgende link: https://ugent.qualtrics.com/jfe/preview/previewId/58fa0fb0-c154-450d-9cf7-f9db8be514ed/SV_elHedwi9JNINgea?Q_CHL=preview&Q_SurveyVersionID=current (https://ugent.qualtrics.com/jfe/preview/previewId/58fa0fb0-c154-450d-9cf7-f9db8be514ed/SV_elHedwi9JNINgea?Q_CHL=preview&Q_SurveyVersionID=current) En bevat na een korte inleiding volgende vragen:
Moodboard Test + (Wireframe)
Vraag: “Welk moodboard voelt het meest passend aan voor dit type toestel in een zorgcontext?”
- Wat je toont: Een wireframe van het product (eenvoudig, zonder stijl) + 3–5 verschillende moodboards (kleur, materiaal, look & feel).
- Wat je meet: doelgroepverwachtingen omtrend CMF.
- Type test: Visuele associatie, brand alignment.
Moodboards in download folder
Preference Test met schaal
Vraag: Op een schaal van 1 tot 7 (1 = totaal niet, 7= zeer veel), in welke mate straalt elk model volgens u betrouwbaarheid uit? Onthoud goed welk ontwerp je de hoogste score geeft, dat is belangrijk voor de volgende vraag.
- Wat je toont: mock-up-renders van verschillende varianten van het toestel.
- Wat je meet: Voorkeur
- Type test: Pairwise comparison + Likert-schaal
Foto’s honden toevoegen 2 per voorbeeld
Desirability Test met Woordkaarten
Vraag: Kies 3 tot 5 woorden uit de lijst die volgens u het best passen bij het ontwerp dat in de vorige vraag het hoogste scoorde
- Wat je meet: Emotionele associaties met esthetiek.
- Waarom waardevol: Geeft zachte, menselijke feedback op vormgeving.

Calming
Calm
Supportive
Friendly
Professional
Discrete
Clear
Abstract
Natural
Pleasant
Trustworthy
Innovative

Positive
Recognizable
Warning
Annoying
Intimidating
Unprofessional
Boring
Creative
Exciting
Impressive
Fresh

### 5 Second Test met

Vraag: “Wat is uw eerste indruk van dit product?”
- Wat je toont: Werkingsvideo van het fysieke prototype gedurende 5 seconden, daarna mening gevraagd.
- Wat je meet: Spontane, intuïtieve perceptie van esthetiek.
- Type test: First impression / emotion mapping

# Bijlagen

[1] Hu, H., Liu, Y., Lu, W. F., & Guo, X. (2022). A quantitative aesthetic measurement method for product appearance design. Advanced Engineering Informatics, 53, 101644. https://doi.org/10.1016/j.aei.2022.101644
[2] Chan, M. (2025, March 27). Testing Visual Design: A Comprehensive guide. Nielsen Norman Group. https://www.nngroup.com/articles/testing-visual-design/

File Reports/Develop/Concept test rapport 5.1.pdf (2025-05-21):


Vak: Gebruiksgericht ontwerpen Design Challenge: Werkbaar werk in de zorg

Docenten: Bastiaan Baccarne & Yannick Christiaens

Studenten: Demaegdt Pieter, Schrijvers Finn, Tops Bram

# Concept test rapport 5.1

# Inleiding

Dit rapport kadert binnen het vak Gebruiksgericht Ontwerpen, met als thema "Werkbaar werk in de zorg". Het project 'Take Five' heeft als doel burn-out bij zorgverleners die onder hoge werkdruk werken, te analyseren en te bestrijden. Het systeem bestaat uit drie componenten: een wearable die het stressniveau meet, een feedback unit die de status visualiseert, en een verificator die pauzes voorstelt en logt. Deze specifieke test, Concept Test 5.1, bevindt zich in de develop-fase en richt zich voornamelijk op het ergonomische aspect van de feedback unit, met name hoe deze zo esthetisch mogelijk kan passen binnen de zorgcontext van woonzorgcentra en ziekenhuizen

# Doel:

In het opgestelde testprotocol Concept (https://ugentbe-my.sharepoint.com/personal/bram_tops_ugent_be/Documents/2024-2025/Gebruiksgericht%20Ontwerpen/D5/Concept%20test%20protocol%205.1.docx) test protocol 5.1 staat beschreven welke methodes het best gebruikt kunnen worden voor deze test. In dit rapport worden de inzichten uit de test geanalyseerd en op basis daarvan wordt een conclusie gevormd.

# Methode (n=35):

De test werd uitgevoerd middels een online enquête via Qualtrics. De doelgroep voor deze enquête (n > 30) bestond uit vrienden, familieleden en studenten, waarbij getracht werd verschillende leeftijdsgroepen te betrekken.

Om het "query effect" te minimaliseren, waarbij de volgorde van vragen of geringe verschillen tussen opties de resultaten beïnvloeden, werden de visuele inputvarianten per testtype voldoende contrasterend gekozen. Deelnemers kregen vooraf een korte introductie over het doel van het onderzoek en de context van de feedback unit, waarbij expliciet werd vermeld dat de test focuste op esthetische en visuele perceptie, niet op technische functionaliteit.

De enquête bevatte verschillende altitudinale testtypen:
•Moodboard A/B Test: Hierbij werd een wireframe van het product getoond, samen met 3-5 verschillende moodboards om doelgroep verwachtingen rond CMF te meten.
•Preference Test met schaal: Mock-up renders van verschillende varianten van het toestel werden getoond, waarbij deelnemers de 'soundness/reliability' moesten beoordelen op een schaal van 1 tot 7. Dit meet de voorkeur.

•Desirability Test met Woordkaarten: Deelnemers moesten 3 tot 5 woorden kiezen uit een lijst die volgens hen het best pasten bij het ontwerp dat in de vorige vraag het hoogst scoorde. Dit meet emotionele associaties met esthetiek.

•5 Second Test: Een werkingsvideo van een fysiek prototype werd gedurende 5 seconden getoond, waarna gevraagd werd naar de eerste indruk. Dit meet spontane, intuïtieve perceptie van esthetiek.

# Materiaal:

Enquête: https://ugent.qualtrics.com/app/comms-navigator/surveys/SV_elHedwi9JNINgea/anonymous-links

# Ruwe data

Te vinden in: data (https://ugentbe-my.sharepoint.com/personal/bram_tops_ugent_be/Documents/2024-2025/Gebruiksgericht%20Ontwerpen/D5/f11f8200-120c-4199-883a-ca5e051e30ae.pdf)

# Ontwerpvragen

Welke esthetiek roept rust of vertrouwen op in een zorgcontext?
De Concept Test 5.1 had als doel om de Feedback Unit esthetisch te laten aansluiten bij de omgeving van woonzorgcentra en ziekenhuizen, met aandacht voor CMF (Color, Material, Finish), vorm en stijl.

Volgens de resultaten van de Moodboard Test (Q1) werd Figuur 1: Moodboard1 als het meest passend ervaren voor een apparaat in een zorgcontext. Dit moodboard vertegenwoordigt de CMF en de look & feel die het beste aansluiten bij de verwachtingen van de doelgroep.

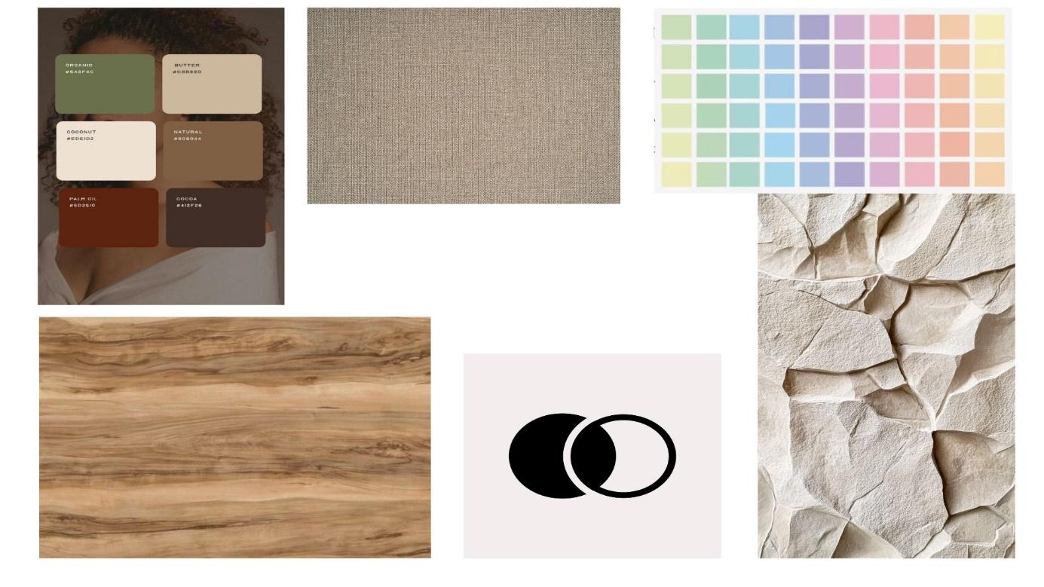
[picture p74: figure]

Figuur 1: Moodboard1

Uit Test 3.2 kwam naar voren dat het ontwerp gebruik moest maken van een metafoor die positieve emoties oproept, met nadruk op het opwekken van joy en rust. Dierlijke metaforen zoals dolfijnen en vlinders, evenals de koffietas, werden positief gewaardeerd. De gekozen metafoor moet rustgevend zijn en een gevoel van vertrouwen en kalmte oproepen.
In Test 4.1 werd onderzocht hoe signalen worden geïnterpreteerd. Daaruit bleek dat kleurgebruik een belangrijke rol speelt: groen werd als rustgevend ervaren, warm wit als zacht en aangenaam. Kleuren als blauw en rood werden daarentegen eerder negatief geïnterpreteerd. Daarnaast kregen abstracte, niet-kinderachtige dierfiguren de voorkeur, evenals rustgevende bewegingen van de metafoor.

Welke stijl sluit aan bij de mentale modellen van zorgverleners?
Test 5.1 was gericht op het verzamelen van richtlijnen voor een stijl die aansluit bij de mentale modellen van zorgverleners.
De Moodboard Test (Q1) toonde aan dat Moodboard 1 als het meest passend werd ervaren, wat suggereert dat de stijl van dit moodboard overeenkomt met de verwachtingen van de doelgroep. Uit Test 4.1 bleek dat abstracte dierfiguren die niet kinderachtig overkomen, de voorkeur genieten.
Daarnaast gaf Test 3.2 aan dat het gebruik van een metafoor, zoals een dier of koffietas, rust en joy moet oproepen, wat aansluit bij de gewenste emotionele associaties van zorgverleners.

Welke vorm en afwerking straalt betrouwbaarheid uit?
Test 5.1 had ook als doel om inzicht te krijgen in welke vorm en afwerking als betrouwbaar worden ervaren.
De Preference Test met schaal (Q2) in het bronbestand mat de perceptie van betrouwbaarheid. Apparaat 1 behaalde hierin de hoogste gemiddelde score (5.12 op een schaal van 1 tot 7), wat aangeeft dat dit apparaat als het meest betrouwbaar werd beoordeeld.

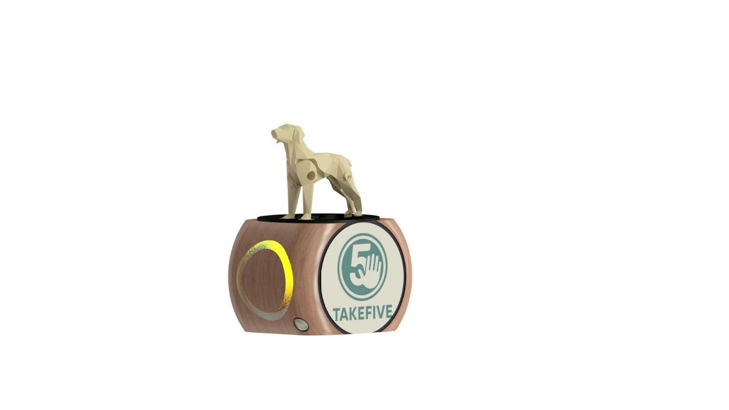
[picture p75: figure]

Figuur 2: apparaat 1

Test 3.1 leverde aanvullende designvoorwaarden voor betrouwbaarheid, zoals het gebruik van een stevig scharnier, duidelijke lichtkleurindicaties en een robuuste fysieke constructie die bestand is tegen water, stoten en vallen.
Daarnaast liet Test 4.1 zien dat bewegingen intuïtief en positief geïnterpreteerd moeten worden. Bewegingen die negatieve emoties oproepen, zoals een olifantenslurf die omhooggaat (wat angst kon opwekken), zijn onwenselijk.

Welke gevoelens roept het ontwerp op?
Voor het meten van emotionele associaties met het ontwerp werd in Test 5.1 de Desirability Test met Woordkaarten (Q3) ingezet. De kernwoorden hierbij waren de volgende:

- Kalmerend
- Natuurlijk
- Vriendelijk
Deze kwamen voor bij bijna 50% van de antwoorden.
Ook geven eerdere tests, zoals Test 3.2, aan welke gevoelens het ontwerp idealiter moet oproepen: positiviteit, aanmoediging, vertrouwen, herkenning, kalmering, ontspanning en persoonlijke betrokkenheid, met een duidelijke focus op het opwekken van joy en rust. Wat is de initiële indruk van het ontwerp?
De 5 Second Test uit Test 5.1 was bedoeld om de spontane, intuïtieve eerste indruk van het prototype te meten. Deze zijn weergegeven als wordcloud in Figuur 3: wordcloud.

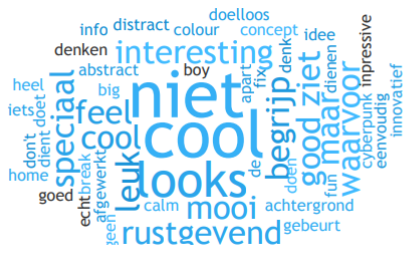
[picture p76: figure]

Figuur 3: wordcloud

Eerdere bevindingen, met name uit Test 4.1, gaven aan dat de functie van de Feedback Unit zonder uitleg niet altijd meteen duidelijk was – wat wenselijk bleek in het kader van discretie – maar dit zegt niets over de esthetische eerste indruk.

# Conclusie

Q1 Het uiteindelijk product gebruikt best een natuurlijke uitstraling naar materiaalafwerking toe. Verder geniet het ook van pastel-/aardetinten. Naar materiaalkeuze toe geven hout en stof goede uitstraling weer. Daarnaast worden er best ronde vormen gebruikt

Q2 baseert het ontwerp verder op het moodboard uit Q1 en volgt dus dezelfde redenering.

Q3 - Desirability Test met Woordkaarten: Bij deze test werden deelnemers gevraagd 3 tot 5 woorden te kiezen die het ontwerp met de hoogste score (Apparaat 1 uit Q2) het best beschrijven. De gekozen woorden die het best passen zijn natuurlijk, kalmerend en vriendelijk. Dit zijn de exacte waarden die het product moet uitstralen.

Q4- hieruit blijkt dat veel mensen het prototype een coole uitstraling vinden hebben, maar bijna geen één weet wat het doet, het is dus te abstract voor bezoekers en duidelijk genoeg naar het personeel toe.

Over het algemeen zijn alle resultaten binnen de verwachtingen en aligneren deze met de eerder gestelde conclusies in vorige rapporten.

# Design requirements

Op basis van de gesprekken met het zorgpersoneel en de directeur zijn de volgende design requirements opgesteld.
ID | Design Requirements | Mo SC oW | Source | Date
DR52 | Het ontwerp van moet rust en vertrouwen uitstralen door: gebruik te maken van ronde vormen. | M | Test 5 | 17/05/2025
DR2 | Het kleurgebruik moet natuurlijke kleuren zoals pastel- of aardetinten bevatten. | M | Test 5 | 17/05/2025
DR3 | De gebruikte materialen moeten er natuurlijk uitzien zoals bijvoorbeeld: hout en stof | S | Test 5 | 17/05/2025
DR4 | Afwerkingen mogen niet te glanzend of kil zijn. | S | Test 5 | 17/05/2025

# Bijlagen

[1] Hu, H., Liu, Y., Lu, W. F., & Guo, X. (2022). A quantitative aesthetic measurement method for product appearance design. Advanced Engineering Informatics, 53, 101644. https://doi.org/10.1016/j.aei.2022.101644
[2] Chan, M. (2025, March 27). Testing Visual Design: A Comprehensive guide. Nielsen Norman Group. https://www.nngroup.com/articles/testing-visual-design/

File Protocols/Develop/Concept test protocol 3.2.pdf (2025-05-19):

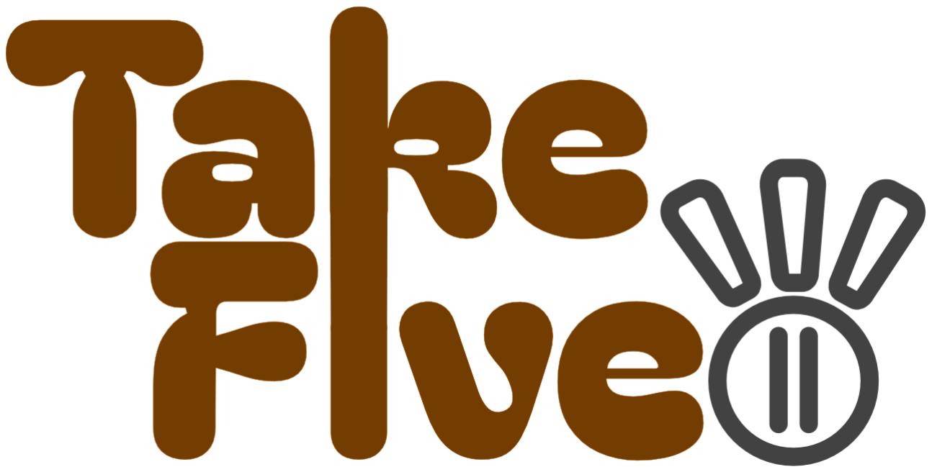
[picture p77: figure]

Vak: Gebruiksgericht ontwerpen Design Challenge: Werkbaar werk in de zorg Docenten: Bastiaan Baccarne & Yannick Christiaens Studenten: Demaegdt Pieter, Schrijvers Finn, Tops Bram

# Concept test protocol 3.2

# Inleiding

Dit concept test protocol wordt gekaderd binnen het vak gebruiksgericht ontwerpen met als thema: “Werkbaar werk in de zorg”. Take five heeft twee doelen, het analyseren, maar ook het bestrijden van burn-out bij zorgverleners die werken onder een hoge werkdruk. Dit gebeurd d.m.v. 3 componenten een wearable die het stressniveau meet, een feedback unit die de status van alle gebruikers visualiseert, en een verificator die doordachte pauzes zal voorstellen en loggen.
Deze test bevind zich in de develop-fase waar voornamelijk het ergonomische aspect wordt onderzocht. Hierbij ligt de primaire focus op de feedback unit. Dit omvat fysieke, cognitieve en sensorische ergonomie.

# Concreet is het doel van deze test om een antwoord te krijgen op de

# Methode (n=5):

Voorgaande concepttest heeft aangetoond hoe de feedbackunit moet functioneren en welke kernkwaliteiten essentieel zijn. Nu is het cruciaal om de meest geschikte metafoor vast te leggen die deze feedbackunit representeert. Om tot de beste keuze te komen, worden methoden ingezet voor het achterhalen van betekenisvolle en contextgevoelige metaforen. Zo wordt via antroposemiotiek onderzocht hoe zorgverleners betekenis geven aan vormen en bewegingen. Emotional mapping wordt ingezet om emotionele reacties op verschillende metaforen in kaart te brengen. Daarnaast zorgt A/B-testing ervoor dat concrete ontwerpvarianten systematisch worden vergeleken.
Eerst worden de Wizard of Oz prototypes getoond (3 in 1), vervolgens worden de bijhorende metaforen getoond (verschillende papieren afbeeldingen). Zorgverleners plaatsen deze op Plutchiks Wheel of Emotions, wat inzicht geeft in de gepercipieerde emotionele impact. Tegelijkertijd worden er doelgerichte vragen opgesteld om te achterhalen welk gevoel precies gewenst is.
Hierbij is het de bedoeling om het gewenst gevoel te koppelen aan de metafoor die dat gevoel het meest representeert.

### Materiaal:

- Plutchiks Wheel of Emotions op A3-papier
- Prototypes: (feedbackunit met verschillende uitvoeringen in 1)
- Informed consent
- Foto’s
- Notities

# Prototypes

### Feedback unit

Het prototype is ontwikkeld om te onderzoeken hoe zorgmedewerkers discrete signalen waarnemen en welke voorkeuren zij daarbij hebben. Voor het ontwerp diende 'Little Signals' van Google¹ als inspiratie, omdat dit concept op een subtiele manier signalen vormgeeft.
Het prototype bevat drie verschillende actuatoren, die elk een ander type beweging en communicatievorm simuleren. Ze worden handmatig bediend via de achterkant:
- Cilinder | -> abstracte vorm
- Op- en neergaande foto | -> beeldje in de vorm van een metafoor
- Bewegend papier | -> Golvende beweging

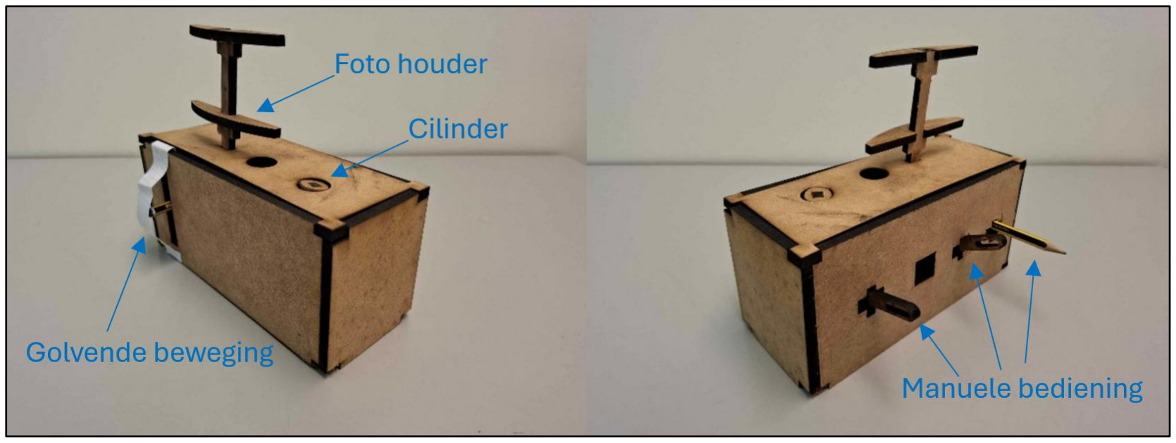
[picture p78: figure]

### Foto’s

De 25 beelden uit de Metaforenlijst worden door zorgverleners op Plutchik's wheel of emotions geplaatst bij het gevoel dat ze oproepen. Hierdoor wordt zichtbaar welke metaforen welke emoties activeren

1 https://littlesignals.withgoogle.com/

# Ontwerpvragen

“Als de mensen mij komen vertellen dat ze 8 verschillende verwelkte bloemen hebben gezien. Dan zwier ik ze buiten.” Atke Hollebeke Directrice WZC Panhuys
Na ondervonden te hebben dat verwelkte bloemen een te herkenbaar en opvallend negatief stigma meedragen. Is er besloten om op zoek te gaan naar een meer passend metafoor dat als indicator kan dienen op de FU.
De Ontwerpvragen die hiervoor gesteld worden in dit protocol zijn op te delen in functionele en emotionele vragen. Hierop zal een antwoord gegeven zal worden in het Concept test rapport 3.2.docx. (https://ugentbe-my.sharepoint.com/:w:/r/personal/bram_tops_ugent_be/Documents/2024-2025/Gebruiksgericht%20Ontwerpen/D3/Test%202/Concept%20test%20rapport%203.2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)

Uit Concept test rapport 3.1 (https://ugentbe-my.sharepoint.com/personal/bram_tops_ugent_be/Documents/2024-2025/Gebruiksgericht%20Ontwerpen/D3/Test%201/Concept%20test%20rapport%203.1.docx) zijn volgende vaststellingen gesteld:

- Het metafoor die geïmplementeerd wordt op de FU moet relateerbaar zijn voor iedereen.
- Er moet een positieve stimulans worden opgeroepen.²²
- De manier van indicatie moet discreet zijn voor familieleden en bewoners maar toch duidelijk zijn voor de gebruiker.
- De feedbackunit (FU) bestaat best uit één centrale unit voor meerdere gebruikers, waarbij de status per persoon apart zichtbaar blijft.

### Hoofdontwerpvragen:

Functioneel: Wat zijn de mogelijke constraints en euvels aan het product?
Emotioneel: Welke emoties wensen de gebruikers terug te zien/ opgeroepen worden door het product?

# Respondenten

Er is telefonisch contact gelegd met WZC Sint Franciscus²

in Deinze. In het rapport van deze test, zullen de respondenten worden beschreven.
Omdat er gewerkt werd met gebruikers werd er een ‘informed consent’ getekend door elke participant. Deze documenten zijn te vinden in het hoofdstuk Fout! Verwijzingsbron niet gevonden. in het Concept test rapport 3.2.docx.. (https://ugentbe-my.sharepoint.com/:w:/r/personal/bram_tops_ugent_be/Documents/2024-2025/Gebruiksgericht%20Ontwerpen/D3/Test%202/Concept%20test%20rapport%203.2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)

# Overzicht & structuur protocol

In dit deel zal het algemene verloop van de test uitgeschreven worden.
- DEEL 1: Inleiding & root-cause-solution
- DEEL 2: Take-five voorstellen & voorselectie metaforen
- DEEL 3: Plutchik’s wheel of emotion: metafoorplaatsing + locatie FU
- DEEL4: optioneel: Constraint-Evaluatie: voor directeur/leidinggevenden
- DEEL 5: Toetsing van geselecteerde metaforen bij acties prototype

https://wzc-sintfranciscus.be/

### Deel 1: Inleiding & root-cause-solution

Vooraf:
- Informed consent invullen
- Spraakopname starten
Inleiding:
Wij willen u eerst en vooral bedanken voor de tijd die u hebt vrijgemaakt om vandaag samen met ons dit onderzoek te doen. We willen je eerst ons project voorstellen waar we dit jaar volop mee bezig zijn.
Wij zijn in Vlaanderen op onderzoek gegaan en hebben gemerkt dat burn-outs vaak voorkomen. De bedoeling van ons project ‘Take Five’ is om d.m.v. stres metingen pauzes voor te stellen om op lange termijn een burn-out te vermijden.
De bedoeling van deze test is om feedback te krijgen op verschillende ontwerpvragen omtrent cognitieve ergonomie.
De antwoorden die we verwachten hebben te maken met de manier waarop de concepten en metaforen worden bevonden. Het is dus zelfs belangrijk om het eerste dat in je opkomt te vertellen.
Root-Cause-Solution:
Tijdens eerder onderzoek is gebleken dat burn-out een gevolg is van te hoge werkdruk. Deze werkdruk is hoofdzakelijk een gevolg is van personeelstekorten. Een tweede oorzaak is te wijten aan een tekort aan voldoening (dit dan natuurlijk bij mensen die aan burn-out leiden).
- Ziet u persoonlijk personeelstekorten als de hoofdoorzaak van werkdruk?
- Zo ja: volgende vraag
- Zo nee: doorvragen
- Stel u beeld zich een gemiddelde werkdag in. Wat zijn dan juist de momenten/aspecten die je voldoening geven?
- Waar is dit dan meestal?
- En met wie?
- Nu even het compleet tegenovergestelde. Stel u start met bijvoorbeeld 4 mensen op een afdeling waar normaal 6 mensen bezig zijn en ervaart hierdoor stress.
- Is deze constant aanwezig? Of duikt deze eerder op en verdwijnt deze later?
- Opduiken en verdwijnen → zijn er specifieke momenten of taken aan te koppelen?

### Deel 2: Take-five voorstellen + voorselectie metaforen

Take-five systeem voorstellen: FU + wearable en verificator. “in deze interviewsessie ligt de nadruk op de FU”

### Uitleg concept

Ons project richt zich op het voorkomen van burn-outs in de zorgsector. We ontwikkelen een wearable die je stressniveau meet en communiceert met een Feedback unit. Deze geeft op zijn beurt aan wanneer er een decompressiemoment mag genomen worden. Dit wordt vervolgens geregistreerd via de verificator.
Het hoofddoel van de interviewsessie van vandaag is het testen van metaforen die kunnen passen bij de FU.
Korte voorstelling productgebruik

### Voorselectie metaforen

Zie hier ongeveer 25 metaforen. De bedoeling is dat u deze ordent in drie categorieën: Rustgevend, werk-stimulerend en geen van beide.

# Deel3: Plutchik’s wheel of emotion: metafoorplaatsing + locatie FU

Uitleg wheel of emotion:
Leg nu voor elk concept uit de categorieën: “rustgevend” en “werk-stimulerend” deze bij de voor u persoonlijk meest passende emotie. De bedoeling is dat dit vlot gaat, dus altijd van de eerste gedachte uitgaan, indien u later toch twijfelt mag dit alijd worden aangepast.
Selecteer nu enkele van je favoriete metaforen
- Wat vind je er juist goed aan?
- Welke metaforen zou u zelf extra toevoegen?
Voorstellen werking feedback-unit:
Hoe zou je deze juist laten werken met de FU?

### Locatie FU:

Oké, we hebben nu normaalgezien een goede stimulator/kalmerend effect gevonden. De vraag die zich nu luid is of u liever constant zou kunnen zien of de FU een mogelijkheid tot pauze bied doordat deze zich op de kar bevindt? Of zou u deze liever op vaste punten op uw route tegenkomen?
- Indien ja: zijn er vaste punten waarop u vaak werkdruk/stress ervaart?
Indien ja: de welke zijn dit dan?
Indien nee: dus dit is eerder tijdsafhankelijk?
- In hoeverre past het systeem naadloos in de bestaande workflow van zorgmedewerkers, zonder extra stress of werkdruk te veroorzaken?

### Deel 4: Constraint-Evaluatie: voor directeur/leidinggevenden

Concept voorstellen Nadrukken dat het systeem geen “god” is en dat de “pauze”-tijd kan worden ingesteld.
In het algemeen, wat vind je van dit idee?
- Wat vind je er goed aan?
- Wat vind je er minder goed aan?
- Wat zou je zelf aanpassen mocht je kunnen kiezen?
- Zie je manieren waarop het product mogelijks niet juist in de omgeving zou passen?
- Zijn er voor u metaforen die naast de huidige metaforen goed zouden passen bij kalmeren of werkstimulatie? (toon lijst)
De wearable zal een PPG-sensor gebruiken. Hiermee kunnen stress en prestaties worden gemeten. Wat zou je willen dat ze met deze data doen?
- Bijvoorbeeld: het welbevinden van een team adhv een tussentijdse/dag stress-samenvatting
- Hoofdfunctie = aankaarten wie kans loopt op burn-out
Voor de locatie van de FU zijn er twee opties: op de zorgkar of op een vaste plaats. Wat zou hiervoor de beste plek zijn?

# Deel 5: Debriefing

Bedankt om deel te nemen aan ons interview.

# Bijlagen:

### Metaforenlijst

Nr. | Afbeelding | Concept | Bevinden

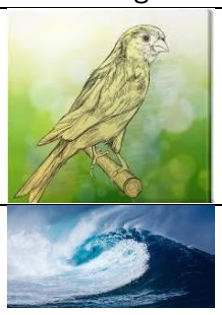
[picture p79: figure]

1 | | Vogel vliegt tijdens goed bevinden. Landt op tak wanneer er pauze moet worden genomen. | Joy,
2 | | Golf beweging met lichtsignaal cfr. Wii disk input
3 | | Kampvuur dat begint te smeulen bij verminderde prestatie en harder brandt naarmate “performantie” | Grieve (kampvuur begint de verminderen)

Lichtgevende balkjes die kunnen pulseren; Amazement; Konijn dat komt kijken uit gat

4 | | Companion die zoals staafje omhoog komt.
6 | | Ventilator die gaat draaien en lucht blaast
8 | | Koffietas die gaat oplichten | Tof ideetje (als je tas beneden vol is heb je weinig stress,

Oplaadanimatie jbl

10 | Lamp die begint te branden/pulseren
11 | Kangoeroe die springt om te stimuleren. Die gaat zitten om te kalmeren | Tof maar hoe is het mogelijk
12 | Constant bewegend object dat plots hard gaat bewegen/stilstaat | Ook iets zoals canariepietje in corona met CO2
13 | Tandwielen die blijven draaien/ vaststuiken/ stoppen | Anger
14 | Hand die omhoog gaat/ gebaar uitdrukt. | Dit is wel een goeien, duidelijk signaal. Anger
15 | Dolfijn die uit het water springt | Joy (de dolfijn jeunt em), joy (hoe hoger hoe leuker),

Vuurvliegje dat begint te pulseren/bewegen; Kompas dat begint te draaien; Fear,; Thermometer die stijgt; Anger

17 | Bloem met bij op die sluit om de bij bij stress
19 | Windmolen die draait | Joy, als het snel draait zou het averechts werken
20 | Vlinder die werkt zoals vogel en rust op bloem | Superlief, blij, met voldoende persoon, trust,
21 | Puzzelstukken die oplichten en naar boven komen.


23 | Luchtverfrisser die geur verspreid o.b.v. stress? | Suprise
24 | Een zon die vanachter de wolken verschijnt | Geeft een goed gevoel, warmte
25 | Een eend die uit het riet verschijnt

### Plutchik's wheel of emotions

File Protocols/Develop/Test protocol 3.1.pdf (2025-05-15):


Vak: Gebruiksgericht ontwerpen Design Challenge: Werkbaar werk in de zorg Docenten: Bastiaan Baccarne & Yannick Christiaens Studenten: Demaegdt Pieter, Schrijvers Finn, Tops Bram

# Concept test protocol 3.1

2

# Inleiding

Dit concept test protocol wordt gekaderd binnen het vak gebruiksgericht ontwerpen met als thema: “Werkbaar werk in de zorg”. Take five heeft twee doelen, het analyseren, maar ook het bestrijden van burn-out bij zorgverleners die werken onder een hoge werkdruk. Dit gebeurd d.m.v. 3 componenten een wearable die het stressniveau meet, een feedback unit die de status van alle gebruikers visualiseert, en een verificator die doordachte pauzes zal voorstellen en loggen.
Deze concepttest bevindt zich deels nog in de definition-fase, aangezien het systeem op basis van eerdere tests is uitgebreid met twee extra componenten. Daarom wordt in eerste instantie opnieuw geëvalueerd of de conceptuele werking van het volledige systeem aanvaardbaar is. Tegelijkertijd bevindt de test zich ook deels in de develop-fase, waarnaast de werking ook het ergonomische aspect wordt onderzocht, hierbij ligt de primaire focus op de feedback unit (=bloem). Dit omvat fysieke, cognitieve en sensorische ergonomie.

### Doel

Concreet is het doel van deze test om een antwoord te krijgen op de ontwerpvragen waarop een antwoord gegeven zal worden in het Concept test rapport 3.1.docx.

# Methode (n=5):

Voor dit onderzoek worden concepttestings, interviews en taakanalyses uitgevoerd met Wizard of Oz-prototypes bij vijf zorgverleners, geselecteerd via purposive sampling. De evaluatie gebeurt zowel kwantitatief als kwalitatief.
Kwantitatief wordt de bruikbaarheid beoordeeld met een korte enquête¹

op basis van de SUS-scales. Kwalitatief wordt onderzocht hoe het systeem wordt gebruikt, met aandacht voor de gebruiksmethode en het vastleggen van het cognitieve framework.
De tests worden uitgevoerd met minimale interferentie voor de deelnemer, volgens de 80/20-regel en het Think Aloud Principle, zodat natuurlijke interactie en gebruikservaring zo goed mogelijk worden geobserveerd.

### Materiaal:

- Enquête (https://ugent.qualtrics.com/jfe/form/SV_e2OXte1L1stqcFo)
- Cognitive framework
- Prototypes: wearable, verificator, feedbackunit, Interfaces op papier
- Informed consent
- Foto’s
- Notities

### 1 https://ugent.qualtrics.com/jfe/form/SV_e2OXte1L1stqcFo

3

# Prototypes

In onderstaande tabel worden alle prototypes beschreven.


Wearable: Bestaat uit een ge-3D-printe body met een elastieken band, deze kan gedragen worden op de bovenarm. Deze wearable meet het stressniveau en zal de status van de feedback unit real time updaten.


Feedback unit (hoofdfocus): Elke gebruiker heeft een eigen bloem op zijn/haar zorgkar staan. De bloem gaat slapper hangen naarmate het stressniveau toeneemt. Zodra de bloem volledig slap hangt zal de kleur van de bloempot rood kleuren, op die moment is het tijd om de bloem water te geven -> pauze nemen.

4

Verificator (gieter):
Wanneer de bloem aangeeft dat het tijd is voor een pauze (door slap te hangen en een rode pot te tonen), moet deze bij de verificator (gieter) worden geplaatst.


De verificator herkent de eigenaar van de bloem en stelt verschillende pauzes voor. De gebruiker kiest een pauze, waarna de verificator de starttijd registreert. Kort voor het einde van de pauze trilt de wearable om aan te geven dat het tijd is om het werk te hervatten.

Hierbij moet de gebruiker de pauze met een knop op de verificator stoppen. Indien de pauze goed is uitgevoerd heeft men water verdiend om de bloem weer gezond te maken (bloem rechtop en pot kleur groen).


Interface:
De verificator bevat een interface die de gebruiker verschillende pauzes kan voorstellen. Tegelijk is dit een systeem dat de pauzes zal loggen om misbruik zoveel mogelijk tegen te gaan.

5

# MoSCoW-Methode

D.m.v. een extra uitgebreide MoSCoW- methode in combinatie met brainstorming en roleplay is er een waardevolle tabel bekomen welke resulteert in concrete ontwerpvragen, design requirements en aandachtspunten voor de concepttests. (Zie MoSCoW tabel in Bijlagen)
In deze MoSCoW-tabel heeft elk teamlid zoveel mogelijk relevante vragen geformuleerd. Vervolgens zijn deze gezamenlijk besproken en beoordeeld, wat heeft geleid tot waardevolle discussies en oplossingen.
Dit proces resulteert in concrete ontwerpvragen, design requirements en aandachtspunten voor de concepttests.
Gezien de omvang van de MoSCoW-tabel, worden de belangrijkste inzichten samengevat in onderstaande sectie Conclusie.

### Conclusie

Designrequirements voor de feedback unit (bloem)
- Moet eenduidig visueel en fysiek signaleren wanneer een pauze mag worden genomen.
- Kan in slaapstand gaan bij uitdoen van de wearable.
- Moet een betrouwbare werking hebben (stevige scharnier i.c.m. lichtkleurindicatie).
- Kan antropomorfische elementen bevatten (bv. slap hangen bij stress).
- Optioneel een dockingstation voor opladen (met micro-interacties zoals pulserend licht).
Designrequirements voor het algehele systeem
- Pauzebeheer: Hoofdverpleegkundige/afdelingshoofd moet de pauzeduur kunnen regelen.
- Interactie: De verificator (gieter) moet strategisch geplaatst worden in de pauzeruimte en/of vlakbij de uitgang indien buitenactiviteiten gewenst zijn.
- Notificaties: Wearable moet een trilsignaal geven als de pauze voorbij is. Signalisaties zullen pas stoppen zodra er op de stopknop is gedrukt op de verificator.
- Data & Privacy: Webapplicatie kan inzicht geven in stressniveaus, maar privacy moet gewaarborgd blijven.
- Oplaadmogelijkheden: Moet voorzien worden van een laadstation.
- Gebruiksvriendelijkheid: Systeem moet intuïtief zijn.
Te testen
- Kan er valsgespeeld worden met de pauze-verificatie?
- Wat is de meest eiciënte manier om interactie met de verificator te starten? (Badge, wearable, bloem)
- Hoe lang duurt de interactie met de verificator en zijn er wachttijdproblemen?

6

- Wordt het als sociaal onaanvaardbaar gezien om zonder de bloem te werken?
- Is het nodig om de feedbackunit fysiek mee te nemen naar de verificator, of is een alternatieve verificatiemethode beter?
- Gebruikerservaring testen: intuïtief gebruik vs. uitleg krijgen.

# Ontwerpvragen

Voorgaande methodologie hebben geleid tot verschillende concrete ontwerpvragen die beantwoord zullen worden d.m.v. deze concept test.
Conceptuele validatie (Definition-fase)
- In welke mate sluit de voorgestelde pauzestrategie aan bij de noden en verwachtingen van zorgmedewerkers? (=wat is de opinie van de gebruiker)?
- Hoe betrouwbaar en consistent functioneert het systeem onder verschillende werkomstandigheden en stressniveaus?
- Welke drempels ervaren gebruikers bij het gebruik van het systeem, en hoe kunnen deze worden verminderd?
- Is een verificator (zie
- Prototypes) noodzakelijk, of volstaat het als de feedbackunit zelf aangeeft welke pauze genomen moet worden, bijvoorbeeld via een geïntegreerd display?
- Kan het systeem omzeild worden (bv. te weinig of te veel pauze nemen) en hoe kan dit e.v.t. worden opgelost?
Ergonomische aspecten (Development-fase)
- Hoe intuïtief en toegankelijk is de interactie met het systeem voor zorgmedewerkers in een veeleisende werkomgeving?
- Welke vorm/uiterlijk van de feedback unit biedt de beste sensoriele ergonomie aan de gebruiker?
- Hoe beïnvloedt dit systeem de cognitieve belasting en werkprestaties?
- Worden de meldingen en suggesties van het systeem als helpend of storend ervaren tijdens het werk?
- Hoe goed past het systeem binnen de bestaande workflow van zorgmedewerkers zonder extra stress of werkdruk te veroorzaken?

7

# Respondenten

Er is telefonisch contact gelegd met WZC Panhuis²

in Gent. In het rapport van deze test, zullen de respondenten worden beschreven.
Omdat er gewerkt werd met gebruikers werd er een ‘informed consent’ getekend door elke participant. Deze documenten zijn te vinden in het hoofdstuk Fout! Verwijzingsbron niet gevonden. in het Concept test rapport 3.1.docx.

# Overzicht & structuur protocol

In dit deel zal het algemene verloop van de test uitgeschreven worden.
- DEEL 1: Inleiding & concept voorstellen
- DEEL 2: Noden en verwachtingen vastleggen door bevraging
- DEEL 3: Productgebruik (unguided, guided, probleemscenario’s)
- DEEL 4: Evaluatie
- DEEL 5: Debriefing

2

https://emeis.be/nl/locaties/woonzorgcentrum/panhuys-park

8

### Deel 1: Inleiding & concept voorstellen

Vooraf:
- Informed consent invullen
- Spraakopname starten
Inleiding:
Wij willen u eerst en vooral bedanken voor de tijd die je hebt vrijgemaakt om vandaag samen met ons dit onderzoek te doen. We willen je eerst ons project voorstellen waar we jaar mee volop mee bezig zijn.
Wij zijn in Vlaanderen op onderzoek gegaan en hebben gemerkt dat burn-outs vaak voorkomen. De bedoeling van ons project ‘Take Five’ is om d.m.v. stres metingen pauzes voor te stellen om op lange termijn een burn-out te vermijden.
De bedoeling van deze test is op met jouw feedback een antwoord te krijgen op verschillende ontwerpvragen.
Het is belangrijk om hierbij te vermelden dat er geen juiste of foute antwoorden zijn op de vragen die we straks gaan stellen. Hou je dus zeker niet in om ons te vertellen wat je denkt of ziet. Als er iets onduidelijk is mag je dit altijd zeggen en ideeën of suggesties zijn altijd welkom zodat we ons project kunnen verbeteren.
Inzichten: werkdag + pauzebeleid
- Neem je soms wel eens pauze tijdens uw werk?
- Wat doe je dan meestal?
- Is dit alleen of met andere collega’s?
- Als je zelf zou mogen kiezen...
- Hoe vaak zou je dan pauze nemen?
- Hoelang zouden deze pauzes dan duren? Hoe ziet voor jou een ideaal werkdag eruit?

9

### Deel 2: Noden en verwachting vastleggen

We zouden je nu graag ons project wat meer in detail voorstellen:

### Eerste reacties op concept

Ons project richt zich op het voorkomen van burn-outs in de zorgsector. We ontwikkelen een wearable die je stressniveau meet en communiceert met een slimme bloem.
Wanneer je stressniveau te hoog wordt, suggereert de bloem een pauze (aangegeven door een rode pot en slappe bloem). Met de verificator (*gieter*) kies je vervolgens de gewenste pauze. Zodra je de pauze correct hebt uitgevoerd, herstelt de bloem zich (witte pot, rechtopstaande bloem) en kun je weer aan het werk.
- Wat is jouw eerste reactie op dit idee?
- Wat vind je goed?
- Wat vind je minder goed?
- Waar stel je je eventueel nog vragen bij? Wat is onduidelijk?
- Wat verwacht je eigenlijk van deze plant?
- Hoe verwacht je dat deze er uit zal zien?
- Wat verwacht je dat deze plant kan?
- Kijk je er naar uit om dit product zelf uit te proberen?
- Waarom wel/niet? Leg uit. Wanneer zou je hier gebruik van maken?
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

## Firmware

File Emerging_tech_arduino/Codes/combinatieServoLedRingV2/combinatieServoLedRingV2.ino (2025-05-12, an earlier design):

//Bram Finn Pieter

/*
Aansluitingen:
ledStrip: GND (Grijze kabel) -> GND arduino, 5V (Witte kabel) -> 5V arduino, D (Paarse kabel) -> pin 6
Servo: GND (zwarte kabel) -> GND arduino, 5V (rode kabel) -> 5V arduino, Signaal (Oranje kabel) -> pin 9
IRsensor: GND met GND, 5V met 5V, Output (linker pootje)-> pin 8

Installeer de libraries:
"Adafruit_NeoPixel.h", 
"IRremote" by shirriff, z3to, ArminJo
"Servo" by Micheal Margolis, Arduino

Met behulp van een IR-bakje kan je het besturen.
De servo kan aangestuurd worden met het bakje.
Als de servo maximaal staat, zal de stresswaarde 10 zijn anders is het tussen de 1 en 9.
Tussen 1-9 zal de ledRing groen pulseren, wanneer het 10 is zal het oranje pulseren.
*/

#include <IRremote.hpp>
#include <Servo.h>
#include <Adafruit_NeoPixel.h>

#define IR_RECEIVE_PIN 8
#define SERVO_PIN 9
#define LED_PIN     6
#define LED_COUNT   12

Adafruit_NeoPixel strip(LED_COUNT, LED_PIN, NEO_GRB + NEO_KHZ800); // aanmaak van neoPixel
Servo servo;// aanmaak van servo

int stresswaarde =1; // varieert tussen 1 en 10
int RoodGB= 0;
int RGroenB= 0;
int RGblauw=0;
int pos = 0;
int stapRichting=1;

uint32_t Kleur_Ledring = strip.Color(0, 0, 0);    
unsigned long vorigeTijd = 0;
unsigned long tijd=0;
unsigned long tijdsVerschil=0;


void setup() {
  Serial.begin(9600);
  IrReceiver.begin(IR_RECEIVE_PIN); // IR sensor een pin geven
  servo.attach(SERVO_PIN); // Servo een pin geven
  pos = servo.read();       // neem huidige positie als startpunt
  strip.begin(); // led-ring wakker maken
  strip.show(); // LEDs uit
}

void loop() {

tijd=millis();// werken met Millis voor delay te vervangen -> focus op 16 keer pulseren per minuut (ademhalingsritme) -
tijdsVerschil= round(tijd-vorigeTijd);
if (tijdsVerschil >= 18.75) {
    vorigeTijd = tijd;
}


if (IrReceiver.decode()) {
    int cmd = IrReceiver.decodedIRData.command;
    int oldPos = pos;

    if (cmd == 7) pos = min(pos + 10, 180);         // omhoog
    else if (cmd == 21) pos = max(pos - 10, 0);     // omlaag
    else if (cmd == 12) pos = min(pos + 16, 180);
    else if (cmd == 24) pos = min(pos + 32, 180);
    else if (cmd == 94) pos = min(pos + 48, 180);

    if (pos != oldPos) {// posten van nieuwe hoek in monitor
      stresswaarde = map(pos, 0, 180, 1, 10);// Stresswaarde aanpassen
      servo.write(pos);
      Serial.print("Nieuwe hoek: ");
      Serial.println(pos);
      Serial.println(stresswaarde);

    }

    IrReceiver.resume();
  }


// Rustig groen pulserend 
// Groen 50 naar 255
if (stresswaarde !=10 && tijdsVerschil>18.75){// 18.75 -> 16 keer pulseren per minuut (ademhalingstempo)
  if (RGroenB>=255) {stapRichting =-1;} // eenmaal het maximaal heeft bereikt 
  else if (RGroenB<=50) {stapRichting =1;}
  RGroenB = RGroenB + stapRichting * 2.05; // 2.05= (255-50)/100
  RGroenB = constrain(RGroenB, 50, 255); // extra veiligheid

  Kleur_Ledring = strip.Color(0, RGroenB, 0); // RGB-code toekennen aan een variable
  besturingLedring(12, Kleur_Ledring); // variable doorsturen naar zelfgemaakte functie die ledRing aanstuurt (zie onder void loop)
}

// Hoge stresswaarde pulserend
// Rood 80 naar 255
// Groen 10 naar 60
if (stresswaarde==10 && tijdsVerschil>18.75) {
  if (RoodGB>=254) {stapRichting = -1;}
  else if (RoodGB<=80) {stapRichting = 1;}
  RoodGB = RoodGB + stapRichting * 1.75;
  RGroenB = 10+ (RoodGB-80)/3.5;// RGroenB is afhankelijk van RoodGB
  RoodGB = constrain(RoodGB, 80, 255);
  RGroenB = constrain(RGroenB, 10, 60);

  Kleur_Ledring = strip.Color(RoodGB, RGroenB, 0);
  besturingLedring(12, Kleur_Ledring);
}

}// haakje van void loop

void besturingLedring(int aantalLeds, uint32_t kleur) {
  for (int i = 0; i < LED_COUNT; i++) {
      strip.setPixelColor(i, kleur);
    } 
  strip.show();
  }

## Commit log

2025-03-02 Rename Testprotocol-de oever.pdf to Protocols/Testprotocol-de oever.pdf
2025-04-29 Rename Testprotocol-de oever.pdf to Wave 2 Protocol De Oever.pdf
2025-05-19 een 'we' verwijdert
